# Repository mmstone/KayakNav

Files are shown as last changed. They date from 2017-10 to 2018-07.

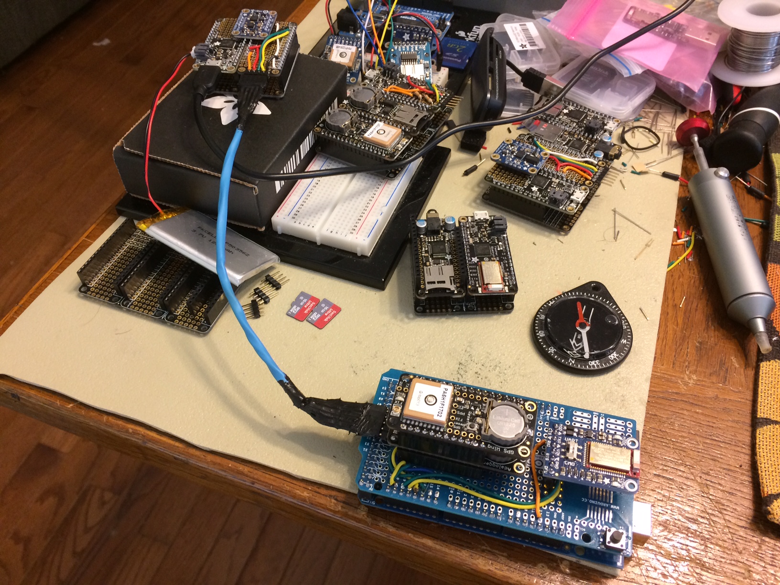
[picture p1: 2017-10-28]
Docs/Photos/IMG_2344.JPG

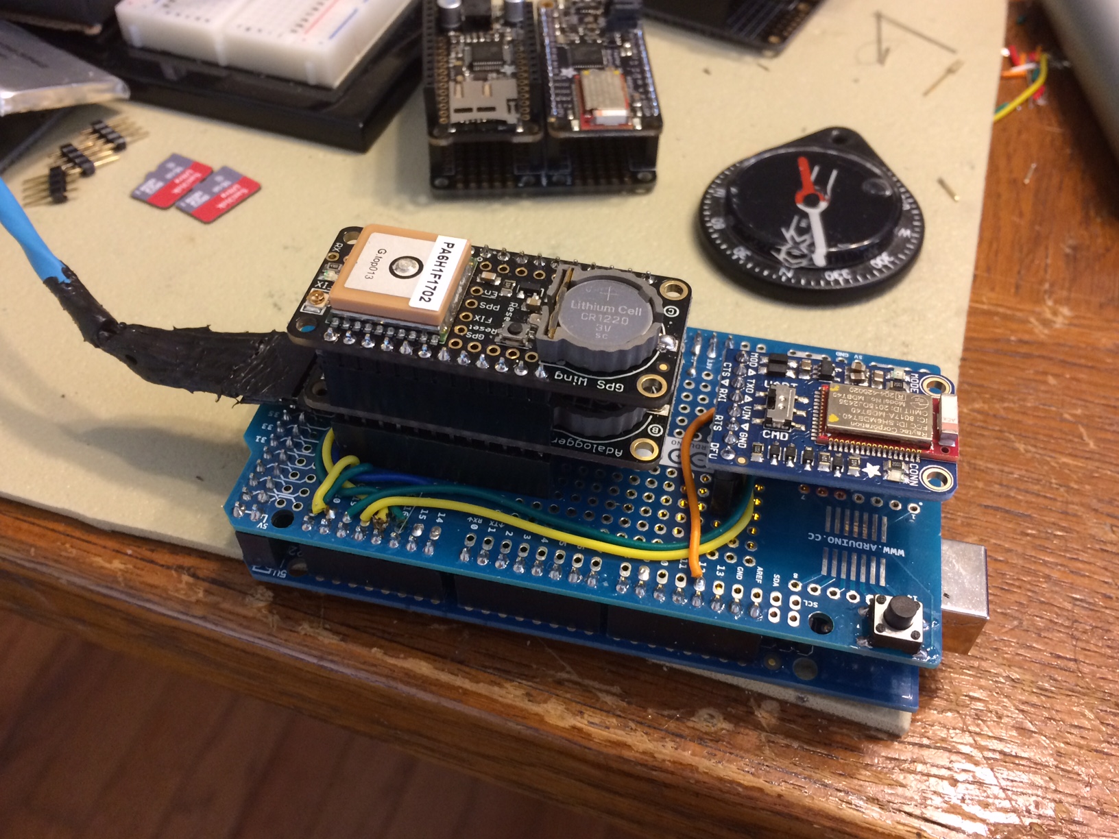
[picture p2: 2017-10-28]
Docs/Photos/IMG_2343.JPG

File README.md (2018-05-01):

# KayakNav
ROGER:  Real-time Onboard GPS Enabled Rowing

Kayak Navigation System Production Code
ROGER Kayak Navigation System Description, Design, Development, and Testing related files and information.

KayakNav subsystems are named in honor of Roger Keeney (founder of A.I.R.S., a 501(c)3 non-profit), 
who initially conceived of the idea for the development of a system to enable the visually disabled to compete
in kayak racing, leading to the development, in 2013, of the "Course Keeper" by volunteers of the Atlanta HACEMOS 
Chapter, another 501c(3).

This system is being developed by Atlanta HACEMOS Chapter volunteers to assist Ahmet Ustunel, a 2017 Holman Prize recipient, 
with his goal to be the first blind person to solo kayak from Europe to Asia (or vice versa).

Offered Completely Open Source and License Free.  
Absolutely no liability, guarantee, or warranty expressed or implied for the use or misuse of this software.
Users assume all responsibility.  Subject to change without notice.  Batteries not included.  Your mileage may vary.
Overall hardware design/build and some code by Martin Stone, amateur Maker, tinkerer, and old, grumpy geek.  Other (more important) code is being provided by Shaoda (James) Yu, who is providing his time, knowledge, and expertise through the Houston IoT Foundry.    

Gratitude to Adafruit and their staff for their products, hardware, software, and support without whom the development
of this system would not be possible.

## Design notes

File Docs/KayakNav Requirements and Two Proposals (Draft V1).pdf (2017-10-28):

STONE, MARTIN, AS OF 8/2/2017 | 1

# KAYAK NAV SYSTEM REQUIREMENTS:

## System Requirements (Functional and User):

Navigation:
- Dedicated Navigational Computer:
- Inertial Measurement Unit (IMU): 3-axis Compass, 3-axis Accelerometer, 3-axis Gyroscope, and on-board Real-Time Clock. Provides heading and distance information, which can be used to compare to GPS for confirm or correction.
- Global Positioning System (GPS): Multi-satellite GPS receiver module. Provides fairly accurate info (+/- 3m or ~10 feet) regarding one’s physical location on earth at a specific point in time.
- System memory to store real-time navigational data, Waypoints, and courses.

User/System Communication:
- Master Computer (with Bluetooth LE)
- On/Off Power/Reset Switch(es)
- 3 x 4 Keypad: Set/Add/Delete Waypoint(s):
- Via Keypad Input (Long./Lat.)
- Via current GPS location
- Create/Save/Delete/Access and begin a Course or Route:
- Via Keypad Input
- Via GPS – route/course/waypoints marked while being performed, and saved as a course.
- Dedicated Sound Processor:
- System communicates via speech to user over Bluetooth:
- While Programming/During Commands: System will walk user through steps to help ensure proper operation
- During active navigation: Provide Speed, Heading, Course Correction Instructions, Waypoints (and proximity), distance completed, distance remaining, rowing time, estimated time remaining, etc., as well as system OK reports.
- Collision avoidance system & warnings: The need is clear, however solution has not been determined.

Power (Source(s) and Consumption):
- Hi-capacity (> ~22000mAh)
- Light weight (Li-ion)

## PROPOSED KAYAKNAV ARCHITECTURE (HIGH-LEVEL): CUSTOM HW AND SW SOLUTION

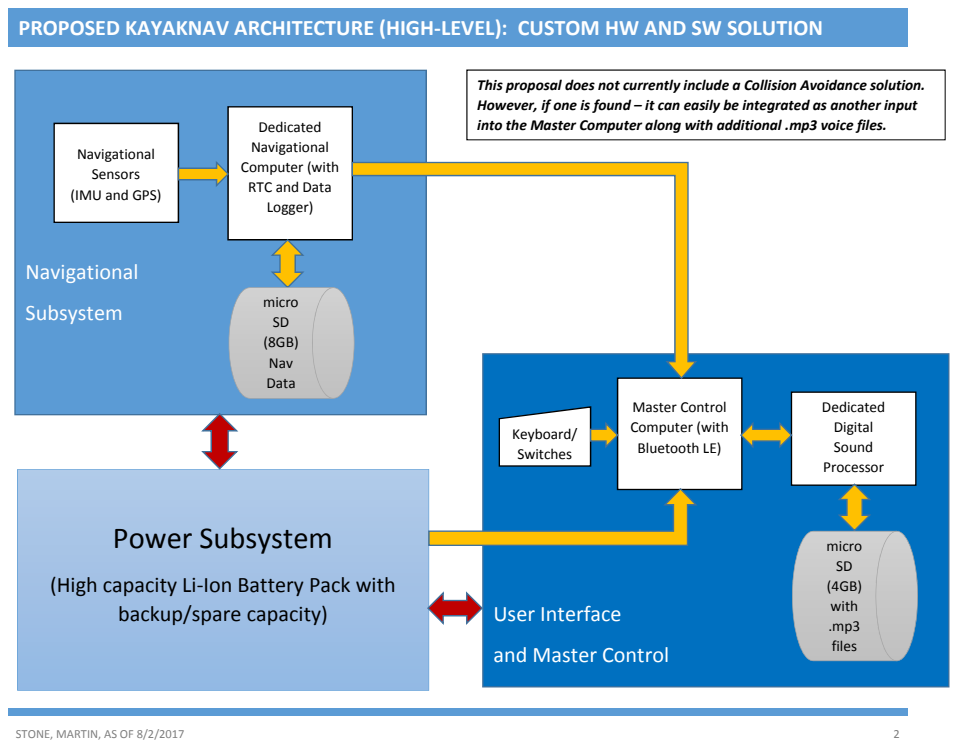
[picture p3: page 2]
STONE, MARTIN, AS OF 8/2/2017; Navigational; Subsystem; micro SD (8GB) Nav Data; User Interface; Dedicated Digital Sound Processor; Master Control Computer (with Bluetooth LE); Keyboard/ Switches; micro SD (4GB) with .mp3 files; Power Subsystem

This proposal does not currently include a Collision Avoidance solution.
However, if one is found – it can easily be integrated as another input
into the Master Computer along with additional .mp3 voice files.

Dedicated
Navigational
Computer (with
RTC and Data
Logger)

Sensors
(IMU and GPS)

(High capacity Li-Ion Battery Pack with

backup/spare capacity)

and Master Control

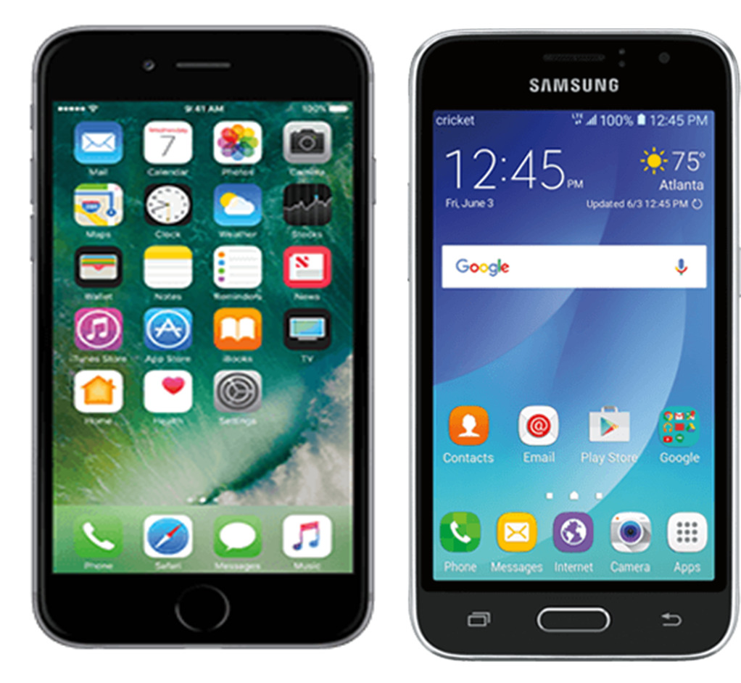
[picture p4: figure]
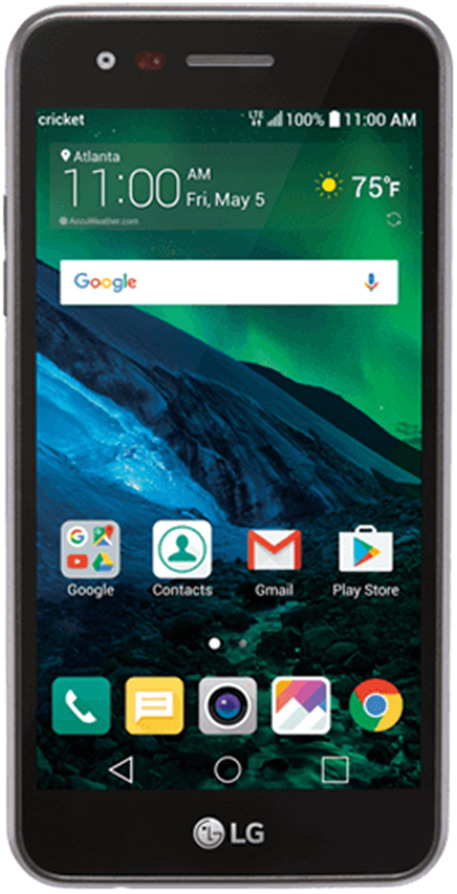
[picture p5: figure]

STONE, MARTIN, AS OF 8/2/2017 | 3

### PROPOSED KAYAKNAV ARCHITECTURE (HIGH-LEVEL): SMARTPHONE AND CUSTOM SOFTWARE SOLUTION

### Option #2:

Develop custom software which can be used on existing Android, Windows or iOS smartphones, enabling a visually impaired person to navigate, set waypoints, and set, plan, save and run through one or more preset courses.

This proposal does not include a Collision Avoidance solution. Such a system would need to be compatible with integration into the smartphone solution (i.e. smartphone HW and SW), once available.

Smartphones are equipped with the necessary navigational sensors (GPS, compass, gyros, and accelerometers) and base software to drive and access these sensors.

Smartphones have Bluetooth capability and Digital Signal Processors (DSPs), built right in.

Smartphones have good battery life and a spare battery pack can be used to ensure no loss of power.

Smartphones can make and accept phone calls – and can also store locally and send real-time data to a cloud database and application.

May be possible to adapt existing smartphone applications like Spyglass or MotionX-GPS (that allow for the setting of courses and waypoints) for use by the visually impaired by providing talking/verbal info instead of visual data (like a map).

Not a custom hardware solution means wider availability.

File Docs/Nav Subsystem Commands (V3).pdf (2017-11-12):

## ROGERNAV Subsystem Command Reference (Draft V3)

Command | Description | Returns
A or a | Altitude (in Meters) above sea level | ALT = MMM
B or b | Backup Battery Voltage | BATT = V.VV
D or d | Current Date (GMT) Leading zeros may be absent | DATE = MM/DD/YYYY
E or e | Latitude/Longitude Format Conversion Error Flags | ERR = E, E
G or g | Current GPS Latitude/Longitude in DDDMM.MMMMX format | GPSLAT = DDMM.MMMM(N/S) GPSLON = DDDMM.MMMM(E/W)
H or h | Current Magnetic Compass Heading, in Degrees | HEAD = DDD.DD
L or l | Current Latitude and Longitude Degrees, Minutes, Seconds | LATDMS = DD,MM,SS.SS LONDMS = DDD,MM,SS.SS
N or n | Stream of vital navigational and system data | Current Date Current Time Current GPS Location Current Heading Current Velocity Altitude Satellites Signal Strength Error Flags
O or o | Other (Decimal) GPS Location Coordinates as DD.DDDDDD | DECLAT = DD.DDDDDD DECLON = DD.DDDDDD
Q or q | Current SD Card Data Record Sequence Number | RSEQ = RRRRRRRRRR
R or r | Current BLE Signal (RSSI) Measurement in dBm | RSSI = SSS
S or s | Number of Satellites with Signal | SAT = SS
T or t | Current Time (GMT) Leading Zeros may be absent. | TIME = HH:MM:SS
V or v | Velocity in Knots | KNOTS = VVV.VV
Anything Else * | Unsupported Request | CMD ERROR

* Current Command list is subject to change, pending development of additional commands and Navigational Subsystem features.

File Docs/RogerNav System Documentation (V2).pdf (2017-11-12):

## RoverNav

Bluetooth LE Capable Navigational Subsystem (Nav Server and Data Recorder):

### 1. Summary of Active Components:

- IMU/9 DOF Precision Sensor
- IMU Processor
- GPS Receiver
- RTC (Real-Time Clock)
- micro SD Card Reader/Writer
- Bluetooth LE Transceiver
- Primary NAV Processor

### 2. Detailed Parts List:

No. | Part Ref# | Description | Qty | Cost | Ext. Amt
1. | 2890 | Adafruit Feather Doubler | 1 | $7.50 | $7.50
2. | 2722 | Adafruit Feather M0 Proto | 1 | $19.95 | $19.95
3. | 2884 | Adafruit Feather Wing Proto Board | 1 | $4.95 | $4.95
4. | 3483 | Adafruit 9-DOF Precision Sensor | 1 | $14.95 | $14.95
5. | 2152366 | Arduino Mega 2560 | 1 | $35.49 | $35.49
6. | 192 | Arduino Mega Proto Shield | 1 | $14.95 | $14.95
7. | 2922 | Adafruit Feather Adalogger | 1 | $8.95 | $8.95
8. | 3133 | Adafruit Feather Wing Ultimate GPS | 1 | $39.95 | $39.95
9. | 2479 | Adafruit Bluefruit LE UART Friend | 1 | $17.50 | $17.50
10. | 258 | Li-ion Backup Battery (3.7V, 1200mAh) | 1 | $9.95 | $9.95
11. | 2693 | 8 or 16GB microSD card Class 10 | 1 | $19.95 | $19.95
12. | 380 | CR1220 Lithium Cell | 2 | $0.95 | $1.90
13. | 2830 | 0.1” pitch female headers | 6 | $1.25 | $7.50
14. | 400 | 0.1” pitch male headers | 1 | $3.00 | $3.00
15. | MSP-N/A | Wire, solder, heat shrink tubing | | $25.00 | $25.00
16. | 960 | Active GPS Antenna | 1 | $12.95 | $12.95
17. NBF- | 32108 | BUD Industries Enclosure | 1 | $21.65 | $21.65
18. | Amazon | USB Li-Ion Primary Battery (10K mAh) | 1 | $16.99 | $16.99
19. | 592 | USB cable – A/MicroB 3 ft | 1 | $2.95 | $2.95
| | | | Total: | $231.49
V2 | AS OF: 11/12/2017

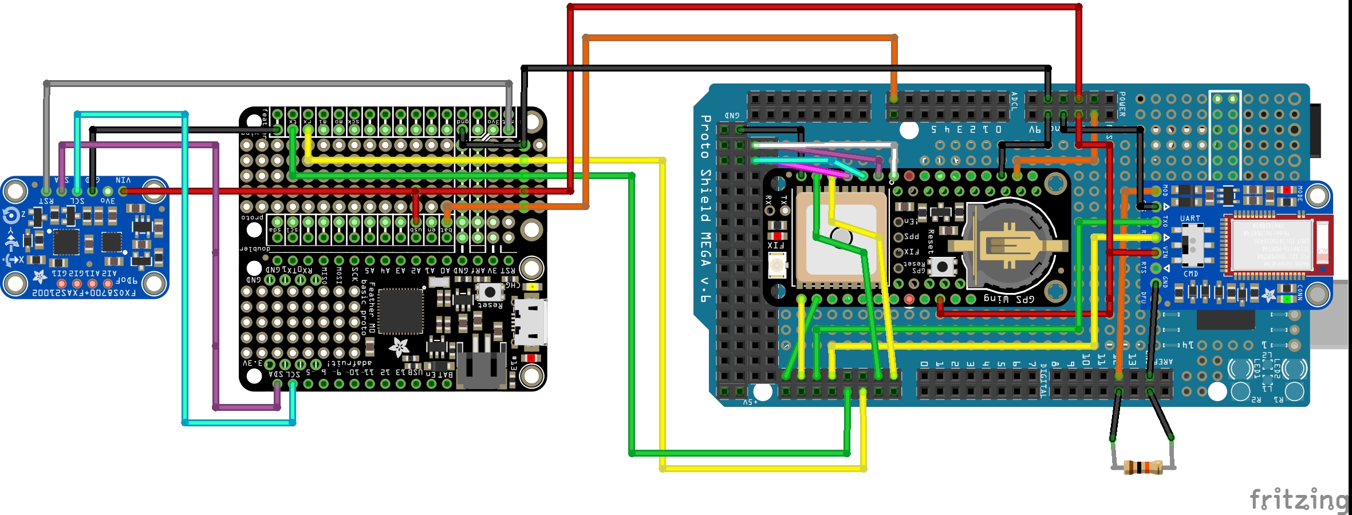
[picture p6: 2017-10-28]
Fritzing/RogerNav01_bb.jpg

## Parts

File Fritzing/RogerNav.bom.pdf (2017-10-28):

# Bill of Materials: RogerNav01.fzz

C:/Users/MStone/Documents/Fritzing/RogerNav01.fzz
Thursday, October 26 2017, 22:18:51

# Assembly List

Label | Part Type | Properties
Part1 | Arduino Mega 2560 (Rev3) | type Arduino MEGA 2560 (Rev3)
Part2 | Adafruit Feather M0 Basic Proto | variant variant 1; part # Adafruit #2772
Part3 | Adafruit FeatherWing Proto | variant variant 1; part # Adafruit #2884
Part4 | Adafruit FeatherWing Doubler | variant variant 1; part # Adafruit #2890
Part5 | Adafruit FXOS8700 + FXAS21002 9 DoF Breakout | variant variant 1; part # Adafruit #3463
Part6 | Adafruit Bluefruit LE UART Friend | variant variant 1; part # Adafruit #2479
Part8 | Adafruit Adalogger FeatherWing | variant variant 1; part # Adafruit #2922
Part9 | Adafruit GPS FeatherWing | variant variant 1; part # Adafruit #3133
Part10 | Arduino Mega Proto Shield (v6) | manufacturer Arduino; shield size Mega
R1 | 10kΩ Resistor | package THT; pin spacing 400 mil; resistance 10kΩ; tolerance ±5%; bands 4

# Shopping List

Amount | Part Type | Properties
1 | Arduino Mega 2560 (Rev3) | type Arduino MEGA 2560 (Rev3)
1 | Adafruit Feather M0 Basic Proto | variant variant 1; part # Adafruit #2772
1 | Adafruit FeatherWing Proto | variant variant 1; part # Adafruit #2884
1 | Adafruit FeatherWing Doubler | variant variant 1; part # Adafruit #2890
1 | Adafruit FXOS8700 + FXAS21002 9 DoF Breakout | variant variant 1; part # Adafruit #3463
1 | Adafruit Bluefruit LE UART Friend | variant variant 1; part # Adafruit #2479
Fritzing Bill of Materials | file:///C:/Users/MStone/Desktop/KayakNav/Fritzing/RogerNav01_bom.html
1 of 2 | 10/26/2017, 10:19 PM

Amount | Part Type | Properties
1 | Adafruit Adalogger FeatherWing | variant variant 1; part # Adafruit #2922
1 | Adafruit GPS FeatherWing | variant variant 1; part # Adafruit #3133
1 | Arduino Mega Proto Shield (v6) | manufacturer Arduino; shield size Mega
1 | 10kΩ Resistor | package THT; pin spacing 400 mil; resistance 10kΩ; tolerance ±5%; bands 4

Exported with Fritzing 0.9.3- http://fritzing.org

Fritzing Bill of Materials | file:///C:/Users/MStone/Desktop/KayakNav/Fritzing/RogerNav01_bom.html
2 of 2 | 10/26/2017, 10:19 PM

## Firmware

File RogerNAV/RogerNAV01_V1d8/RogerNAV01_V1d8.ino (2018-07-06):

////////////////////////////////////////////////////////////////////////////////////////////////////////////////////////
//
//  RogerNAV001_V1d8
//
//  Basic navigational sensors and systems integrated into a data recording and navigational server platform
//  which can be accessed via simple commands via a Bluetooth LE interface.  Navigational sensors include:
//  1)  9-DOF Integrated Sensor (3-axis Magnetometer, 3-axis Accelerometer, 3-axis Gyroscope) w/dedicated M0 processor
//  connected with
//  2)  Arduino MEGA 2560 with:
//      a)  Multi-channel GPS Satellite receiver/signal processor
//      b)  Real-Time Clock (RTC)
//      c)  Micro SD Card Adapter
//      d)  Bluetooth LE Interface
//
//  Changed routine to use the Interrupts
//
////////////////////////////////////////////////////////////////////////////////////////////////////////////////////////
//
//
/////////////////////////////////////////////////////////////////////////////////////////////////////////////////////////
//  #includes
#include <Arduino.h>
#include <SPI.h>
#include <SD.h>
#include <Wire.h>
#include <Adafruit_GPS.h>
#include "RTClib.h"
#include "Adafruit_BLE.h"
#include "Adafruit_BluefruitLE_UART.h"
//
//
//
///////////////////////////////////////////////////////////////////////////////////////////////////////////////////////
//  #defines
#define bleSerial               Serial1  // Bluefruit HW Serial Name
#define imuSerial               Serial2  // IMU HW Serial Name
#define gpsSerial               Serial3  // what's the name of the gps hardware serial port?
#define cardSelect              53       // Card Select on the MEGA for SD Card SPI comm
#define VBATPIN                 A7       // Voltage at the IMU backup battery pin
#define GPSECHO                 false    // Do not echo GPS serial comm data
#define VERBOSE_MODE            true     // If set to 'true' enables debug output
#define FACTORYRESET_ENABLE     1        // Reset = 1.  No resetNo need to reset set it here
#define MINIMUM_FIRMWARE_VERSION    "0.6.6"
#define MODE_LED_BEHAVIOUR          "MODE"
#define BLUEFRUIT_UART_CTS_PIN  8        // Pulled High.  Take low to disable data comm
#define BLUEFRUIT_UART_MODE_PIN 12       // Not used with HW serial
#define BUFSIZE                 128      // Size of the read buffer for incoming data
#define gpsLock                 9        // Pin for LED indicating a GPS Fix.  Take high to activate.
#define sdWrite                 2        // Pin for LED indicating an SD Card write.  Take low to activate.
#define bleXfer                 3        // Pin for LED indicating BLE data is being transferred.  Take low to activate.
#define msgRed                  5        // Pin for Red channel on MSG LED.  Take low to activate.
#define msgGreen                6        // Pin for Green channel on MSG LED.  Take low to activate.
#define msgBlue                 7        // Pin for Blue channel on MSG LED.  Take low to activate.
#define msgSounder              11       // Pin for activating the Piezo sounder.  Take high to activate. 
#define sysLED                  13       // Pin for onboard Arduino LED.  Take high to activate.
//
//
//
// Connect to the GPS on the hardware port
Adafruit_GPS GPS(&gpsSerial);           // Assign the GPS object to the gpsSerial port's address
//
//
RTC_PCF8523 rtc;                        //  Assign the RTC_PCF8523 to the rtc name
//
//
//////////////////////////////////////////////////////////////////////////////////////////////////////////////////////
File logfile;                           //  Assign the File object to the logfile name
//
///////////////////////////////////////////////////////////////////////////////////////////////////////////////////////
//  global data/variables
uint32_t timer         = millis();     // unsigned 32bit interger variable called timer assigned to the millisecond function
uint32_t logRecSeq     = 0;            // used to sequence the record numbers in the log file
uint8_t navHour        = 0;            // current UCT (GMT) hour data from GPS
uint8_t navMinute      = 0;            // current minute data from GPS
uint8_t navSeconds     = 0;            // current seconds data from GPS
uint16_t navMillsec    = 0;            // current milliseconds data from GPS
uint8_t navMonth       = 0;            // current month data from GPS
uint8_t navDay         = 0;            // current day data from GPS
uint16_t navYear       = 0;            // current year data from GPS
uint8_t gpsFix         = 0;            // GPS Sat fix indicator
uint8_t gpsQual        = 0;            // GPS signal quality
float decimalDegLat    = 0;            // Latitude in decimal degrees
float gpsLatitude      = 0;            // GPS Latitude (DDMM.MMMM)
int gpsLatDeg          = 0;            // GPS Latitude Degrees (+/- 90)
uint8_t gpsLatMin      = 0;            // GPS Latitude Minutes (0 - 59)
float gpsLatSec        = 0;            // GPS Latitude Seconds (0 - 59.59)
float decimalDegLon    = 0;            // Longitude in decimal degrees
float gpsLongitude     = 0;            // GPS Longitude (DDDMM.MMMM)
int gpsLonDeg          = 0;            // GPS Longitude Degrees (+/- 179.99)
uint8_t gpsLonMin      = 0;            // GPS Longitude Degrees (0 - 59)
float gpsLonSec        = 0;            // GPS Longitude Seconds (0 - 59.59)
char gpsLat            = ' ';          // GPS North or South indicator
char gpsLon            = ' ';          // GPS East or West indicator
float gpsKnots         = 0;            // GPS Speed in Knots
byte gpsLatError       = 0;            // GPS Latitude Data Conversion Error
byte gpsLonError       = 0;            // GPS Longitude Data Conversion Error
byte batErrCount       = 0;            // Used to throttle the low voltage error message 
float tripMiles        = 0;            // accumulated trip miles traveled
float tripKnots        = 0;            // accumulated trip nautical miles traveled
float tripMeters       = 0;            // accumulated trip meters traveled
float segmentMiles     = 0;            // segment miles traveled (current waypoint to next waypoint)
float segmentKnots     = 0;            // segment nautical miles traveled
float segmentMeters    = 0;            // segment meters traveled
float feetToNextWP     = 0;            // distance in feet to next segment destination point/waypoint
float knotsToNextWP    = 0;            // distance in nautical miles to next segment destination point/waypoint
float milesToNextWP    = 0;            // distance in miles to next segment destination point/waypoint
float metersToNextWP   = 0;            // distance in meters to next segment destination point/waypoint
float gpsAngle         = 0;            // GPS Angle
int gpsAltitude        = 0;            // GPS Altitude (in meters)
uint8_t gpsSats        = 0;            // GPS Satellites
float roll             = 0;            // variable to hold roll data from the IMU
float pitch            = 0;            // variable to hold the pitch data from the IMU
float heading          = 0;            // variable to hold the heading data from the IMU
float qHead            = 0;            // float to hold computed heading from the Quaternion angle
float qW               = 0;            // float to hold the Quaternion angle for heading from the IMU
float qX               = 0;            // variable to hold Quaternion X data from the IMU
float qY               = 0;            // variable to hold Quaternion Y data from the IMU
float qZ               = 0;            // variable to hold Quaternion Z data from the IMU
int utcOffset          = 0;            // offset for local time
int dstAdjust          = 0;            // adjustment for daylight saving time
float measuredVBat     = 0;            // float to hold the measured batttery voltage
const char navName[11] = "RogerNAV01"; // name of the bluetooth LE nav module
const char cmdName[11] = "RogerCMD01"; // name of the bluetoothe LE command module
const int bleBuffSize  = 127;          // size of bluetooth buffer size
int bleRSSI            = 0;            // BLE Signal Strength
//
//
byte bleBuffer[bleBuffSize];           // buffer to hold data to/from the bluetooth comm connection
//
boolean usingInterrupt = false;
boolean bleCMDMode     = false;        // tells you if the Bluetooth LE interface is in CMD mode
boolean stringComplete = false;        // whether the string is complete
boolean dateRefreshed  = false;        // updated when the date is refreshed from GPS
boolean dsTime         = false;        // standard time when false.  daylight saving when true.
boolean trace          = true;         // shows serial print data when true
//
char daysOfTheWeek[7][12] = {"Sunday", "Monday", "Tuesday", "Wednesday", "Thursday", "Friday", "Saturday"};
//
String inputString     = "";           // a string to hold incoming heading data.  Space is allocated in the setup function
//
//  Using HW Serial (Serial1)
Adafruit_BluefruitLE_UART ble(bleSerial, BLUEFRUIT_UART_MODE_PIN);
//
//
////////////////////////////////////////////////////////////////////////////////////////////////////////////////////////
//GPS Interrupt Routines
//
// Interrupt is called once a millisecond, looks for any new GPS data, and stores it
SIGNAL(TIMER0_COMPA_vect) {
  char c = GPS.read();
  // if you want to debug, this is a good time to do it!
#ifdef UDR0
  if (GPSECHO)
    if (c) UDR0 = c;  
    // writing direct to UDR0 is much much faster than Serial.print 
    // but only one character can be written at a time. 
#endif
}
//
//
void useInterrupt(boolean v) {
  if (v) {
    // Timer0 is already used for millis() - we'll just interrupt somewhere
    // in the middle and call the "Compare A" function above
    OCR0A = 0xAF;
    TIMSK0 |= _BV(OCIE0A);
    usingInterrupt = true;
  } else {
    // do not call the interrupt function COMPA anymore
    TIMSK0 &= ~_BV(OCIE0A);
    usingInterrupt = false;
  }
}
//
void useInterrupt(boolean);   // Func prototype keeps Arduino 0023 happy
//////////////////////////////////////////////////////////////////////////////////////////////////////////////////////////
// blink out an error code
void error(uint8_t errno) {
  while (errno != 0) {
    uint8_t i;
    for (i = 0; i < errno; i++) {
      digitalWrite(sysLED, HIGH);
      digitalWrite(msgRed, LOW);
      digitalWrite(msgGreen, HIGH);
      digitalWrite(msgBlue, HIGH);
      sounder(50);
      delay(100);
      digitalWrite(sysLED, LOW);
      digitalWrite(msgRed, HIGH);
      digitalWrite(msgGreen, HIGH);
      digitalWrite(msgBlue, HIGH);
      delay(100);
    }
    for (i = errno; i < 10; i++) {
      delay(300);
    }
    if (errno > 6) {
      errno = 0;
      return;
      }
  }
}
//
//
////////////////////////////////////////////////////////////////////////////////////////////////////////////////////////////
//
void sdCardInit() {
  // see if the card is present and can be initialized:
  if (!SD.begin(cardSelect)) {
    if (trace) {
      Serial.println("Card init. failed!");
    }
    error(2);
  }
  char filename[15];
  strcpy(filename, "NAVDAT00.TXT");
  for (uint8_t i = 0; i < 100; i++) {
    filename[6] = '0' + i / 10;
    filename[7] = '0' + i % 10;
    // create if does not exist, do not open existing, write, sync after write
    if (! SD.exists(filename)) {
      break;
    }
  }
  //
  logfile = SD.open(filename, FILE_WRITE);
  if ( ! logfile ) {
    if (trace) {
      Serial.print("Couldnt create ");
      Serial.println(filename);
    }
    error(3);
  }
  if (trace) {
    Serial.print("Writing to ");
    Serial.println(filename);
  }
  writeHeadingRow();
}
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

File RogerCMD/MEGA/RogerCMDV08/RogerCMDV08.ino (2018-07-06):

////////////////////////////////////////////////////////////////////////////////////////////////////////////////////////
//
//  RogerCMDV08
//
//  Roger Command interfaces to the RogerCMD01 Navigational Subsystem via Bluetooth LE. Commands and Navigational data can
//  be entered via one keypad:
//      1)  4x4 Keypad (used for UI/user commands)
//
//  Along with the two keypads, the main Arduino MEGA 2560 microcomputer is also connected to the following devices:
//      a)  Micro SD Card Adapter
//      b)  Bluetooth LE Interface
//      c)  Serial Rx/TX Connection to an Adafruit Feather M0 Proto connected to an Adafruit Music Maker Featherwing
//          via an Adafruit Feather Doubler - acting as a VRU
//      d)  Open HW Serial Interface (for use by a cell modem for IoT/Geotracking capability)
//      e)  I2C Multiplexer, two 2605 Haptic drivers, and Haptic pancake buzzers
//
////////////////////////////////////////////////////////////////////////////////////////////////////////////////////////
//
//
/////////////////////////////////////////////////////////////////////////////////////////////////////////////////////////
//  #includes
#include <Arduino.h>
#include <avr/wdt.h>
#include <SPI.h>
#include <SD.h>
#include <Key.h>
#include <Wire.h>
extern "C" {
  #include "utility/twi.h"      // from Wire library, so we can do bus scanning
  }
#include "Adafruit_DRV2605.h"
#include <Keypad.h>
#include <TI_TCA9548A.h>
#include "RTClib.h"
#include <ArduinoJson.h>
#include <ctype.h>
//
//
///////////////////////////////////////////////////////////////////////////////////////////////////////////////////////
//  #defines
#define bleCentral              Serial1      // Bluefruit HW Serial Name
#define vruSerial               Serial2      // Adafruit Music Maker HW Serial Name
#define cellSerial              Serial3      // cell module Serial Name
#define cardSelect              53           // Card Select on the MEGA for SD Card SPI comm
#define VBATPIN                 A7           // Voltage at the IMU backup battery pin
#define VERBOSE_MODE            true         // If set to 'true' enables debug output
#define BUFSIZE                 255          // Size of the read buffer for incoming data
#define tcaADDR                 0x70         // Address of TCA MUX
#define sysLED                  13           // Onboard SYSTEM LED and Piezo Buzzer
#define AUTO_RECORD_INT_MS      10000        // 10 sec interval for auto record waypoint
#define PLAYBACK_INT_MS         3000         // 3 sec interval for computing course during playback
#define BLE_WAIT_MS             300          // Time to wait for BLE response n ms
#define TRIP_COMPLETE_INT_MS    10000        // 10 sec interval to let user know trip is complete
#define MODEM_INIT_WAIT         5000         // Time for modem to initialize
#define WAYPOINTS_INIT_LEN      200
#define WAYPOINT_PAGES          10
#define LOC_UPDATE_INT          10000
//
//
////////////////////////////////////////////////////////////////////////////////////////////////////////////////////////
//
//////////////////////////////////////////////////////////////////////////////////////////////////////////////////////////
//  haptic object
Adafruit_DRV2605 drvHap;
//
//
///////////////////////////////////////////////////////////////////////////////////////////////////////////////////
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

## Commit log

2018-04-27 Add case to detect CR along with LF so it'll work for \r\n
2018-05-24 Use pin 12 to reset nRF52 if error
2018-05-31 Added ability to look ahead by 1 waypoint and skip to it if its closer than current waypoint
2018-06-25 Add new feature to get current heading and distance to final waypoint
2018-06-25 Add feature to get current speed in knots
2018-06-30 Add files via upload
    Old sound files - just in case
2019-01-11 Add files via upload
    Adjusted Low Battery Warning value
